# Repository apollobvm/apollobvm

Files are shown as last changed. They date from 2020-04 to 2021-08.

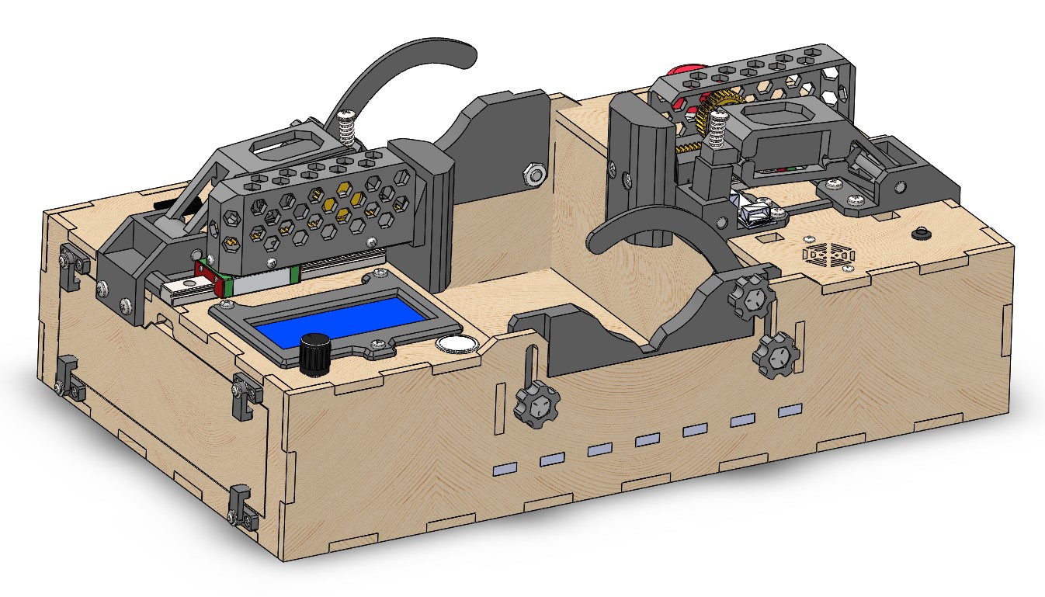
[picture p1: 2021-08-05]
mechanical/Annotation 2020-04-30 215958.jpg

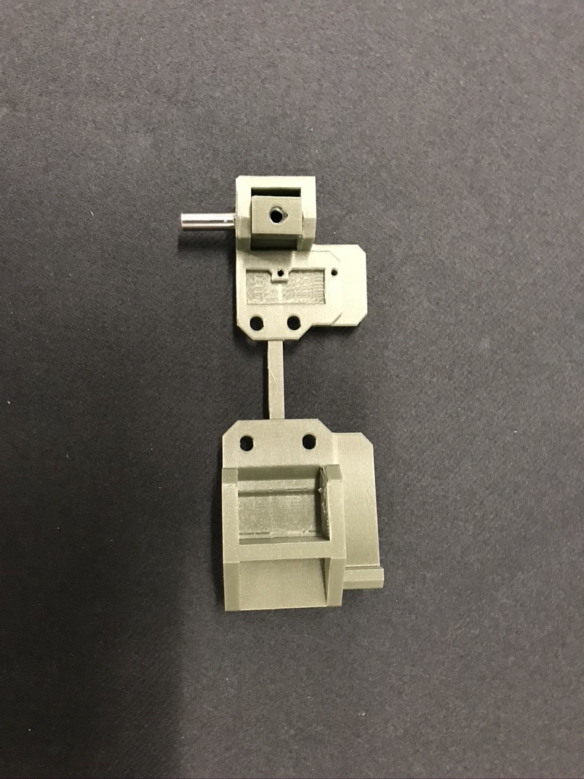
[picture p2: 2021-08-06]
documentation/OEDK - Rice University - ApolloBVM DIY_files/8DABE190-FD51-4D01-BB58-B553A00FD07D_1_105_c.jpeg

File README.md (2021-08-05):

# ApolloBVM - ARCHIVED #
### Rice University Oshman Engineering Design Kitchen ###
###### Author: Thomas Herring ######


<!--[![Build Status](https://github.com/apollobvm/apollobvm/workflows/test/badge.svg)](https://github.com/arduino/arduino-cli-example/actions)-->

**This project is not being actively developed.**

This repository contains all the working code for both the master and slave Arduino to build the ApolloBVM. Feel free to fork it for your own development, we encourage collaboration! All mechanical parts and assembly instructions can be found [here](http://oedk.rice.edu/apollobvm).

For those looking to just download and run the code, please refer to the [releases](https://github.com/apollobvm/apollobvm/releases) section and downloaded the latest firmware. Otherwise, please follow the instructions below on install

For any issues with the code, electrical setup, or mechanical components, please file a bug report [here](https://github.com/apollobvm/apollobvm/issues).

## System Overview ##
The ApolloBVM system uses two coordinated microcontrollers in order to facilitate user input while guaranteeing uninterrupted airflow. The system has a master controller, responsible for managing the display and user input, and a slave controller that actually sends motor commands to the servos. This allows the master controller to operate entirely separately from the slave and ensures that the system is real-time safe. In order to give more clarity about the technical operation of this device, we will outline the operation of each controller separately.

In order to facilitate the various functions of the device, the slave controller operates in 3 distinct states: load, on, and off. While in the ‘load’ state, the slave controller will read ventilation parameters from the master over the I2C bus, generate a new trajectory with these parameters, and turn its state to ‘on’. While in the ‘on’ state, the device will follow the trajectory over and over for infinity. This means that the slave controller will never stop moving the motors unless it receives a command from the master to change its state to ‘stop’. If the master controller were to do so, the device would finish its current cycle and stop moving.

The master controller is mainly tasked with running the user display and sending commands to the slave. Internally, the master switches which panel is currently displaying and manages input from the encoder and buttons. Each panel that the master displays is programmed to follow a different behavior and is modular. This makes it easy to implement panels that behave completely differently and interact with the slave controller on the fly.

## Installation Instructions ##
1. Download the latest Arduino IDE from their website [here](https://www.arduino.cc/en/Main/Software).
2. Download the latest posted release of the device firmware [here](https://github.com/apollobvm/apollobvm/releases), it should look something like "apollobvm_X.X.X.zip".
3. Unzip the downloaded release.
3.  Add the ApolloBVM library to the Arduino IDE:
    1. In the Arduino IDE, go to Sketch->Include Library->Add .ZIP Library...
    2. Navigate to and click on the library zip or library directory inside the extracted release. This will be a file that looks like "ApolloBVM.zip" or a directory with the name "ApolloBVM".
4. Open the slave and master code.
    1. In the Arduino IDE, go to File->Open...
    2. Navigate to and click on the slave.ino file inside the extracted release.
    3. Repeat this process for the master.ino file.
5. Flash the Arduino boards with the firmware.
    1. Plug the first Arduino board into your computer.
    2. In the Arduino IDE, go to Tools->Board and select the Arduino board you are using.
    3. Next, in the Arduino IDE, go to Tools->Port and select the port for your Arduino board.
    4. Push the arrow button to upload code on the Arduino IDE window with the slave code.
    5. Unplug the first Arduino, plug in the second, and repeat the above step for the master code.
6. Follow the wiring diagram on the [ApolloBVM website](http://oedk.rice.edu/apollobvm) to complete assembly.

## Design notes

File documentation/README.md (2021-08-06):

# ApolloBVM Documentation

This directory contrains two website backups that can be viewed locally with
build instructions along with pictures to aid with assembly.

This information is licensed under a
[Creative Commons Attribution 4.0 International (CC-BY-4.0) License](http://creativecommons.org/licenses/by/4.0/).

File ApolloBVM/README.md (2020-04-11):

# Arduino Library for ApolloBVM #

# Credit #
  * Used source code from [Encoder](https://www.pjrc.com/teensy/td_libs_Encoder.html) by Paul Stoffregen Version 1.4.1.
  
# Installation Instructions #
  * In the Arduino IDE, go to Sketch->Include Library->Add .ZIP Library...
  * Navigate to and click on the library zip or library directory inside the extracted release. This will be a file that looks like "ApolloBVM.zip" or a directory with the name "ApolloBVM".

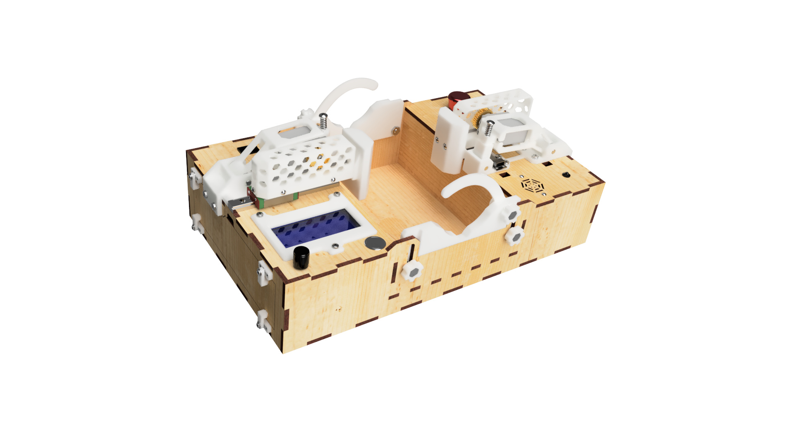
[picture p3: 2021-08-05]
mechanical/ApolloBVM Mk1 - REV1.jpg

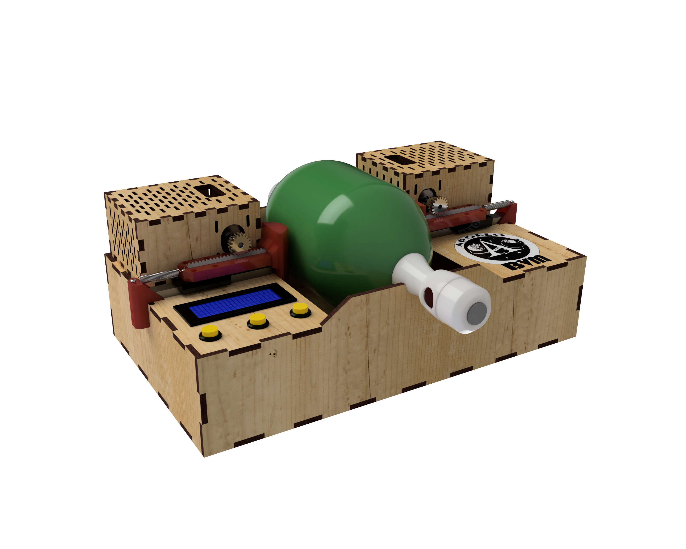
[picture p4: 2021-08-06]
documentation/OEDK - Rice University - ApolloBVM_files/Assem2_OED0011084GX942s_conflicted_copy_2020-03-24_2020-Apr-.jpg

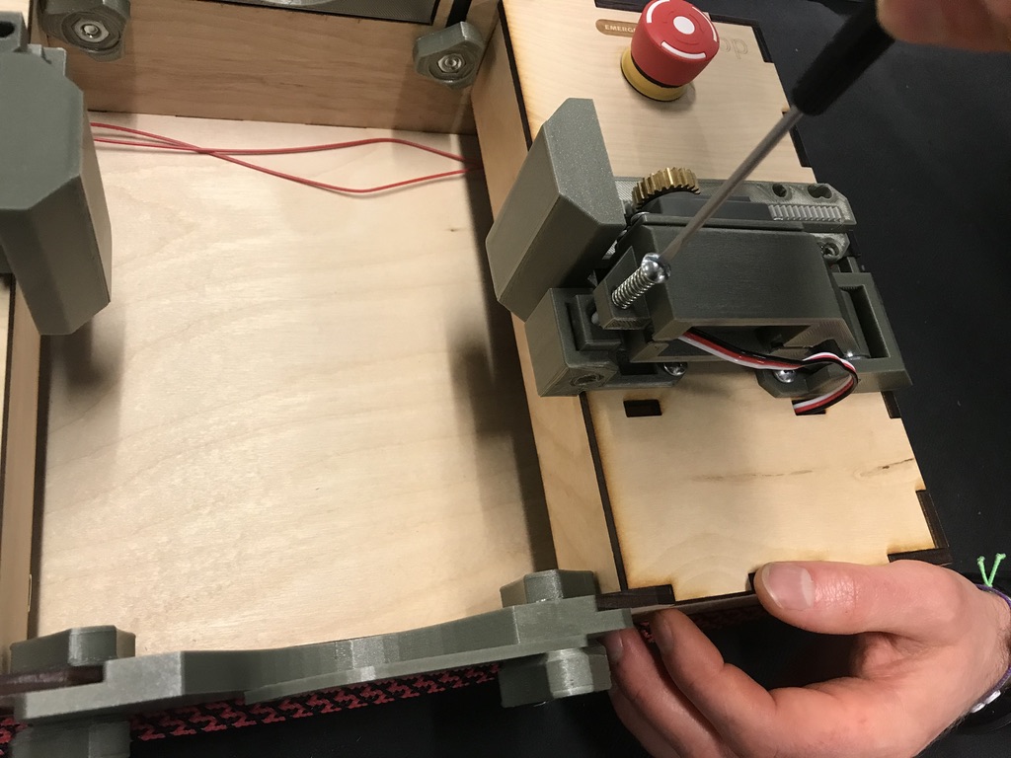
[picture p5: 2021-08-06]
documentation/OEDK - Rice University - ApolloBVM DIY_files/3F8A006A-E7A2-44E5-9089-8951F9FA41A8_1_105_c.jpeg

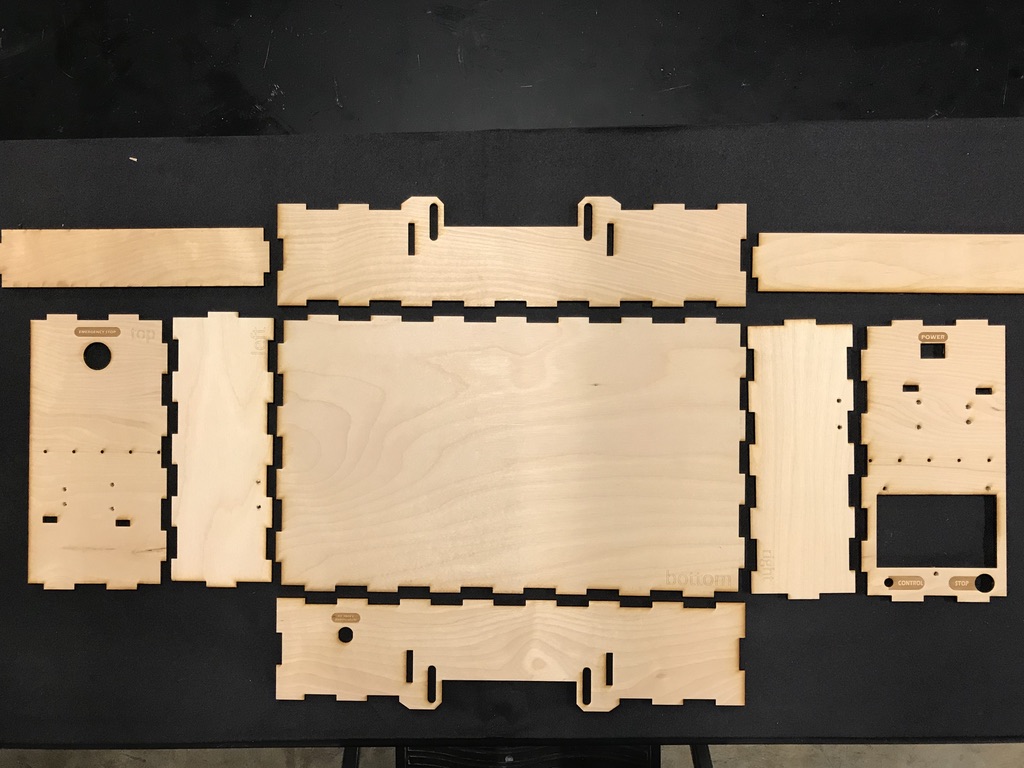
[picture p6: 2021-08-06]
documentation/OEDK - Rice University - ApolloBVM DIY_files/5D290B4A-BDBA-46CC-98D9-BBE2FDADF41D_1_105_c.jpeg

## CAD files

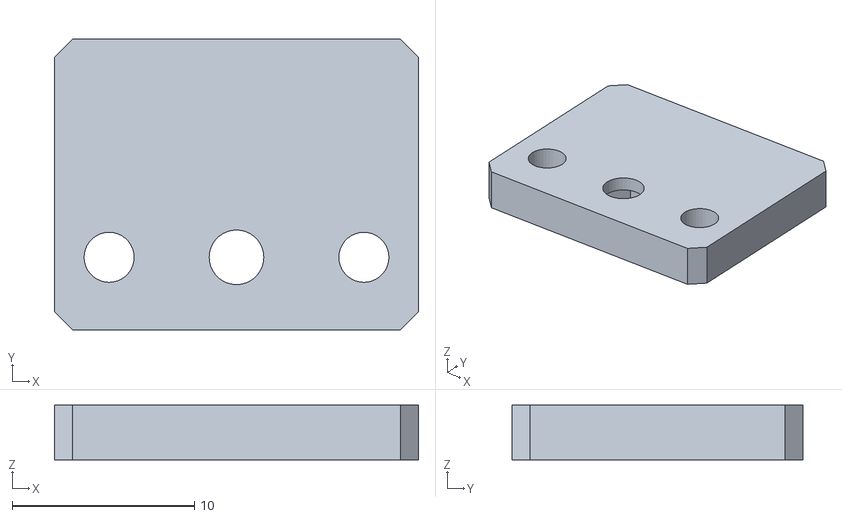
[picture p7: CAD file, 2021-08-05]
mechanical/REV1 STLs/ApolloBVM Mk1 REV1 - Electronics Latch Assembly - Access panel latch - backing.STL
20.0 x 16.0 x 3.00

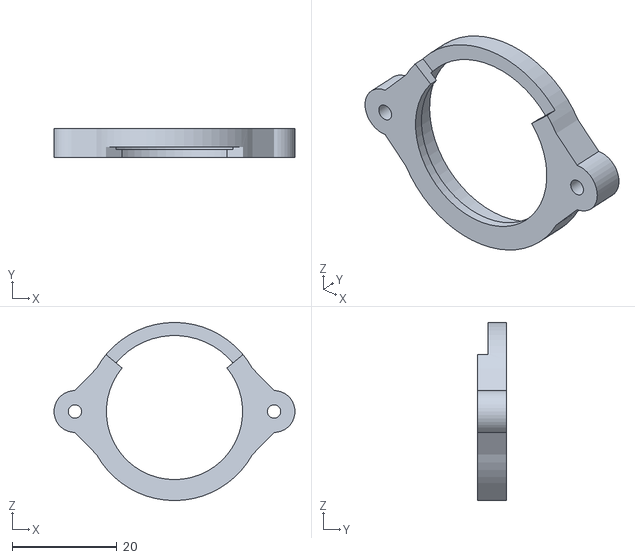
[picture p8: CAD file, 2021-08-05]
mechanical/REV1 STLs/ApolloBVM Mk1 REV1 - Speaker Assembly - Speaker Mount.STL
46.0 x 5.50 x 34.0

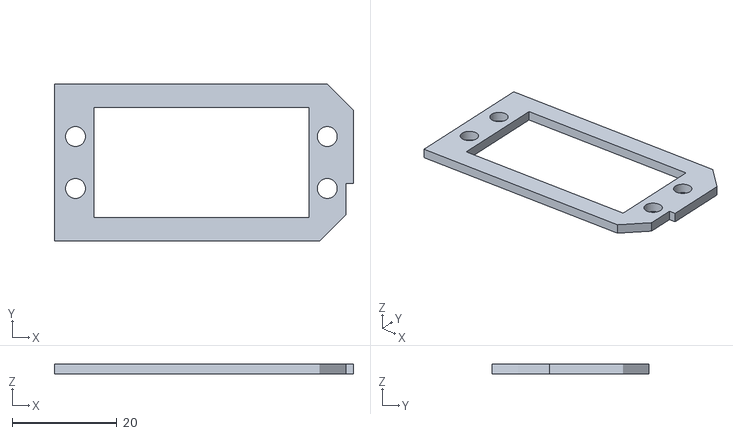
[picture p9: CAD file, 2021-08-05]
mechanical/REV1 STLs/ApolloBVM Mk1 REV1 - Servo Motor Mount Assembly - Servo shim - 2mm.STL
57.0 x 30.0 x 2.00

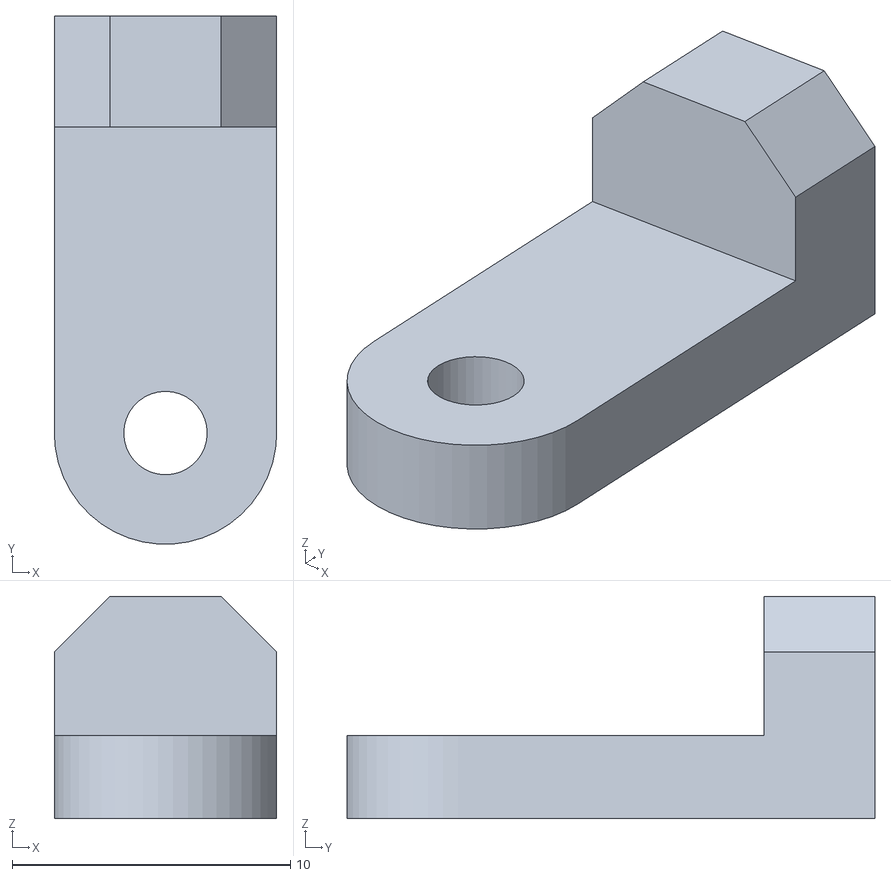
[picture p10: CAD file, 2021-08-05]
mechanical/REV1 STLs/ApolloBVM Mk1 REV1 - Electronics Latch Assembly - Access panel latch - latch.STL
8.00 x 19.0 x 8.00

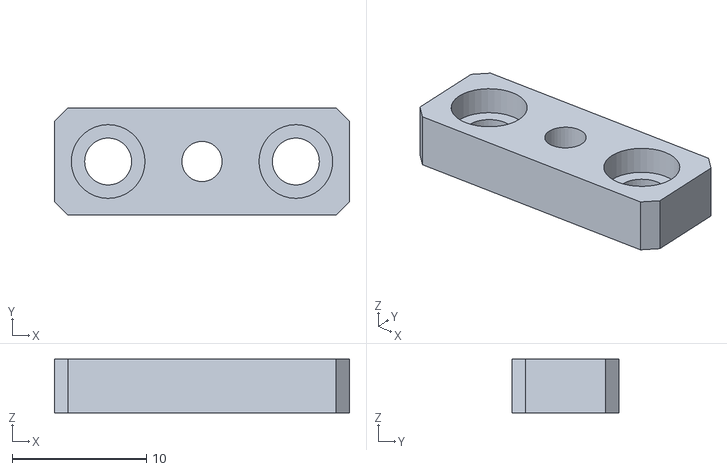
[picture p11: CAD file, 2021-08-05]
mechanical/REV1 STLs/ApolloBVM Mk1 REV1 - Electronics Latch Assembly - Access panel latch - backing front.STL
22.0 x 8.00 x 4.00

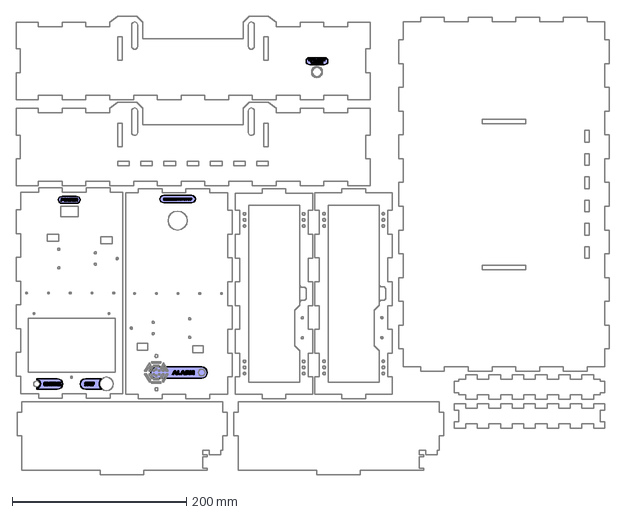
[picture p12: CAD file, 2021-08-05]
mechanical/Laser Cut Pieces/Wood Box - REV1.dxf
680.8 x 526.0 mm

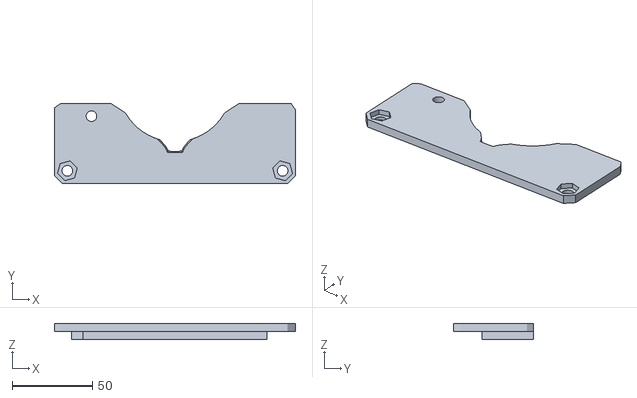
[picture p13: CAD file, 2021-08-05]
mechanical/REV1 STLs/ApolloBVM Mk1 REV1 - BVM Support - Base.STL
150.0 x 50.0 x 10.2

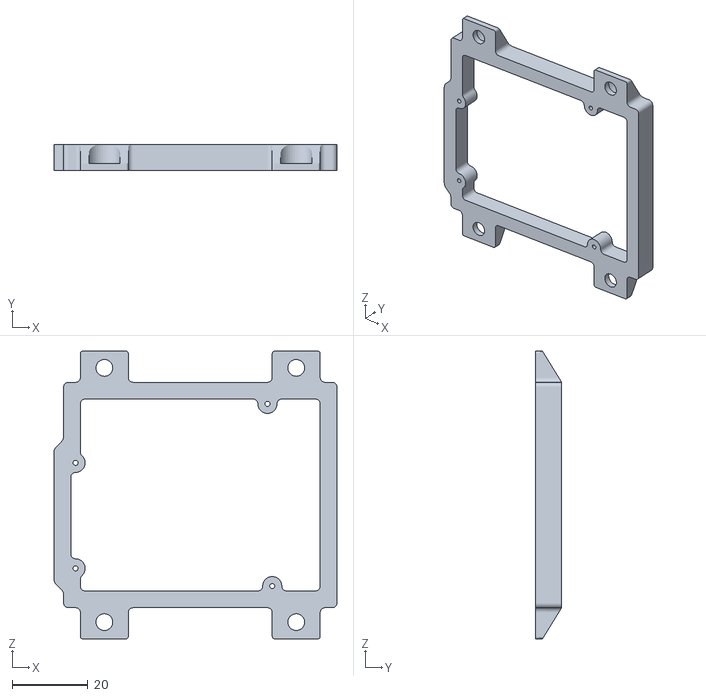
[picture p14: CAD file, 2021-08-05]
mechanical/REV1 STLs/ApolloBVM Mk1 REV1 - Arduino Uno Bracket.STL
74.9 x 6.99 x 76.2

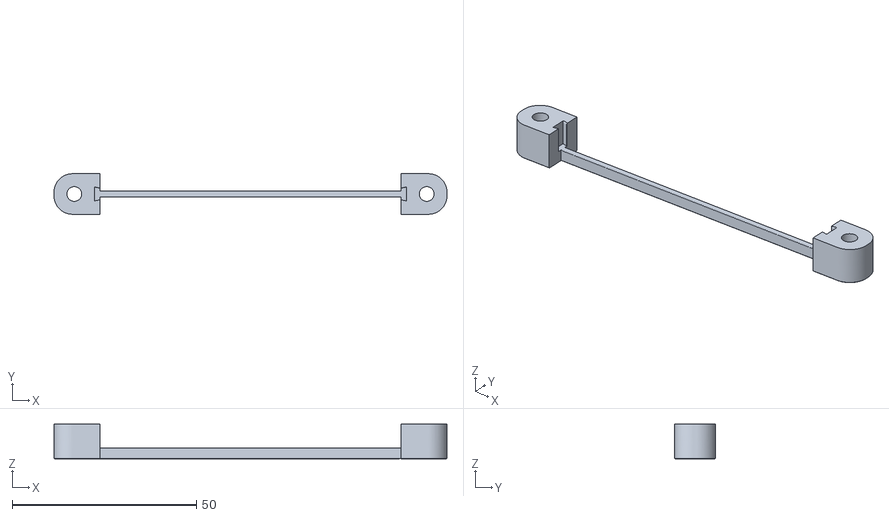
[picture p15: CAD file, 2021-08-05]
mechanical/REV1 STLs/ApolloBVM Mk1 REV1 - Breadboard Brace.STL
106.6 x 11.0 x 9.40

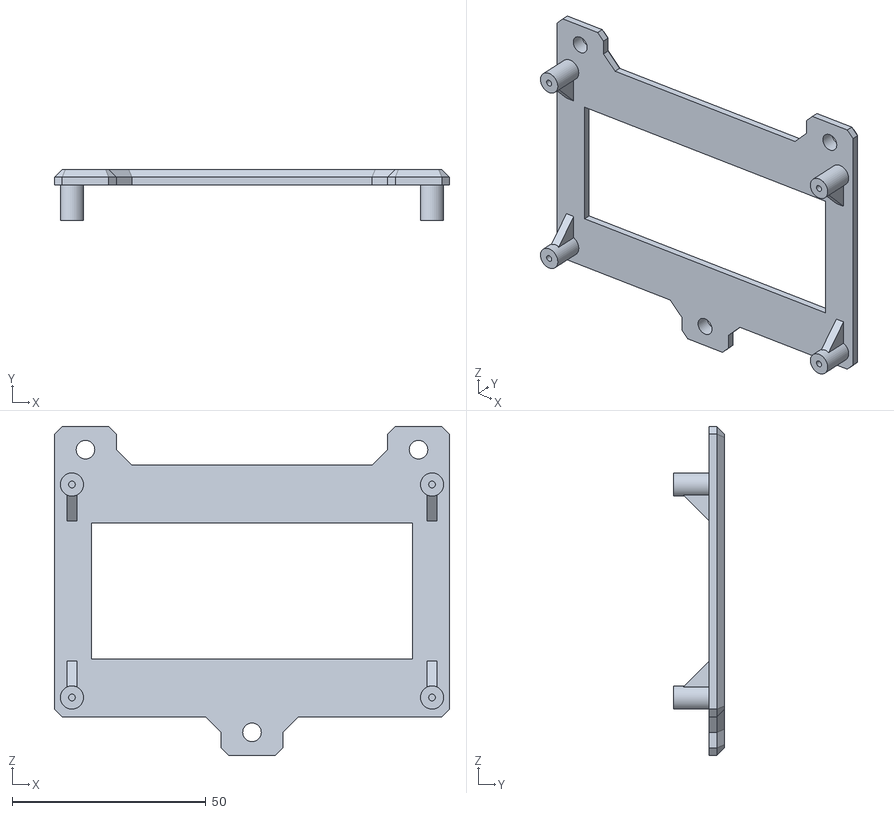
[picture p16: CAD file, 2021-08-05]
mechanical/REV1 STLs/ApolloBVM Mk1 REV1 - Display Cover.STL
102.0 x 13.2 x 85.0

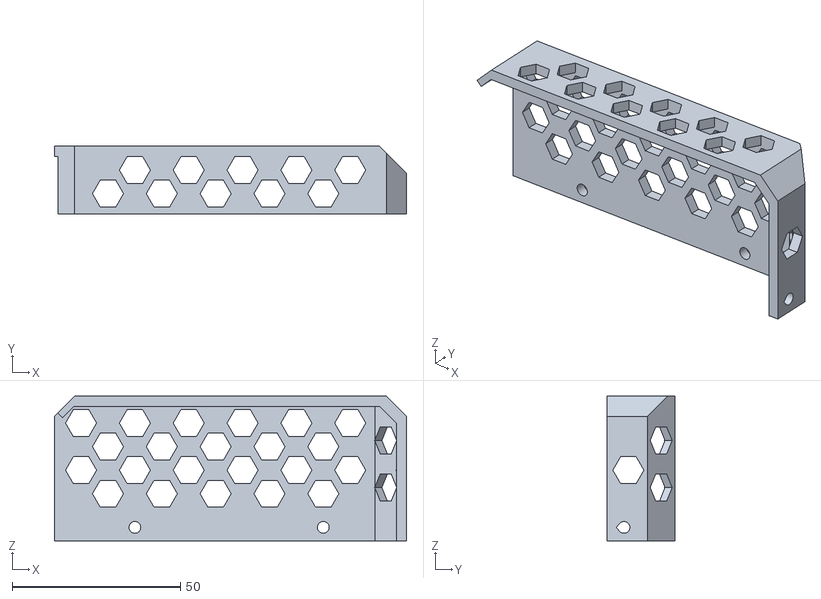
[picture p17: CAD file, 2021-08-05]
mechanical/REV1 STLs/ApolloBVM Mk1 REV1 - Servo Gear Guard.STL
104.6 x 20.1 x 43.0

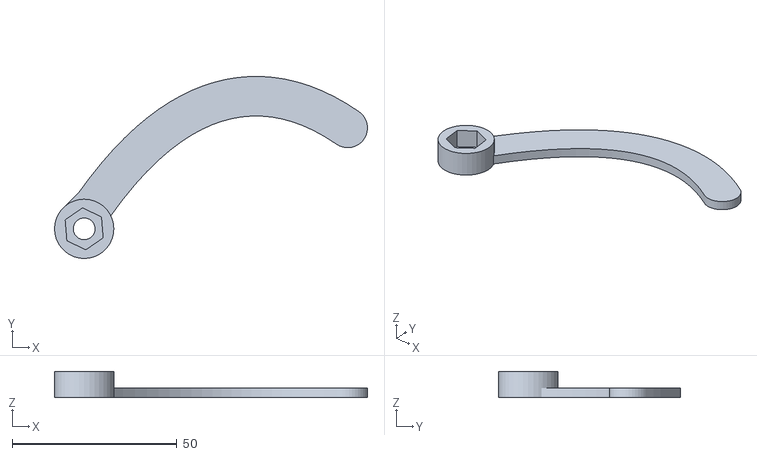
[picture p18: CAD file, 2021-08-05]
mechanical/REV1 STLs/ApolloBVM Mk1 REV1 - BVM Support - Clamp Arm.STL
94.9 x 55.2 x 8.00

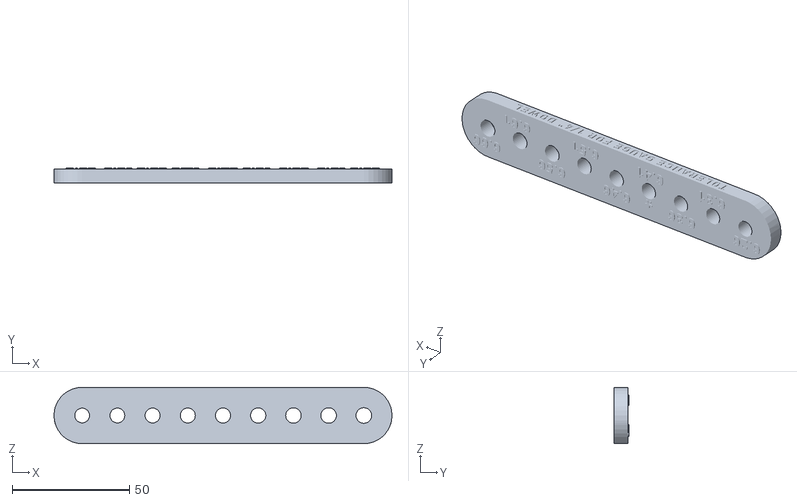
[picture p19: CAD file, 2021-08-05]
mechanical/REV1 STLs/ApolloBVM Mk1 REV1 - Dowel pin tolerance gauge.STL
144.0 x 6.40 x 24.0

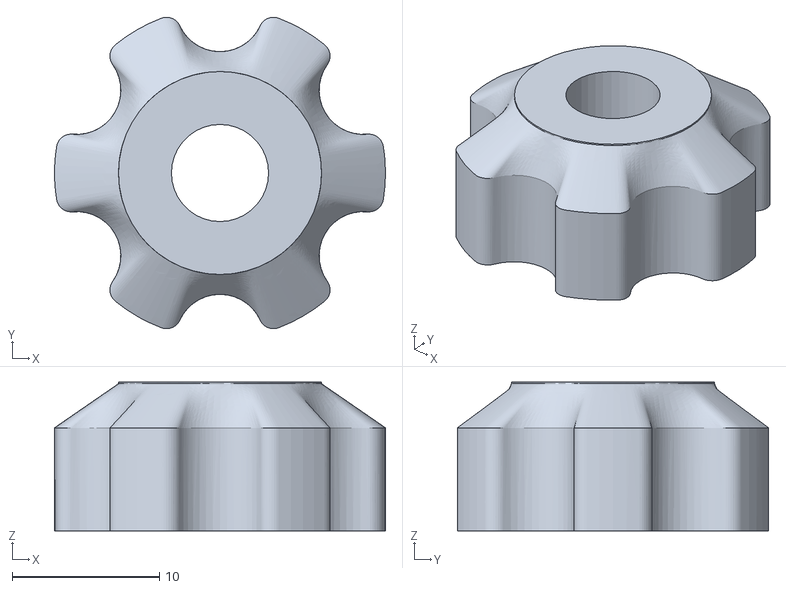
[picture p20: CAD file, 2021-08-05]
mechanical/REV1 STLs/ApolloBVM Mk1 REV1 - Knob - 1_4-20 Hex.STL
22.5 x 21.2 x 10.1

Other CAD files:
mechanical/REV1 STLs/ApolloBVM Mk1 REV1 - Linear Gear Housing Base.STL
mechanical/REV1 STLs/ApolloBVM Mk1 REV1 - Bumper-REV1.STL

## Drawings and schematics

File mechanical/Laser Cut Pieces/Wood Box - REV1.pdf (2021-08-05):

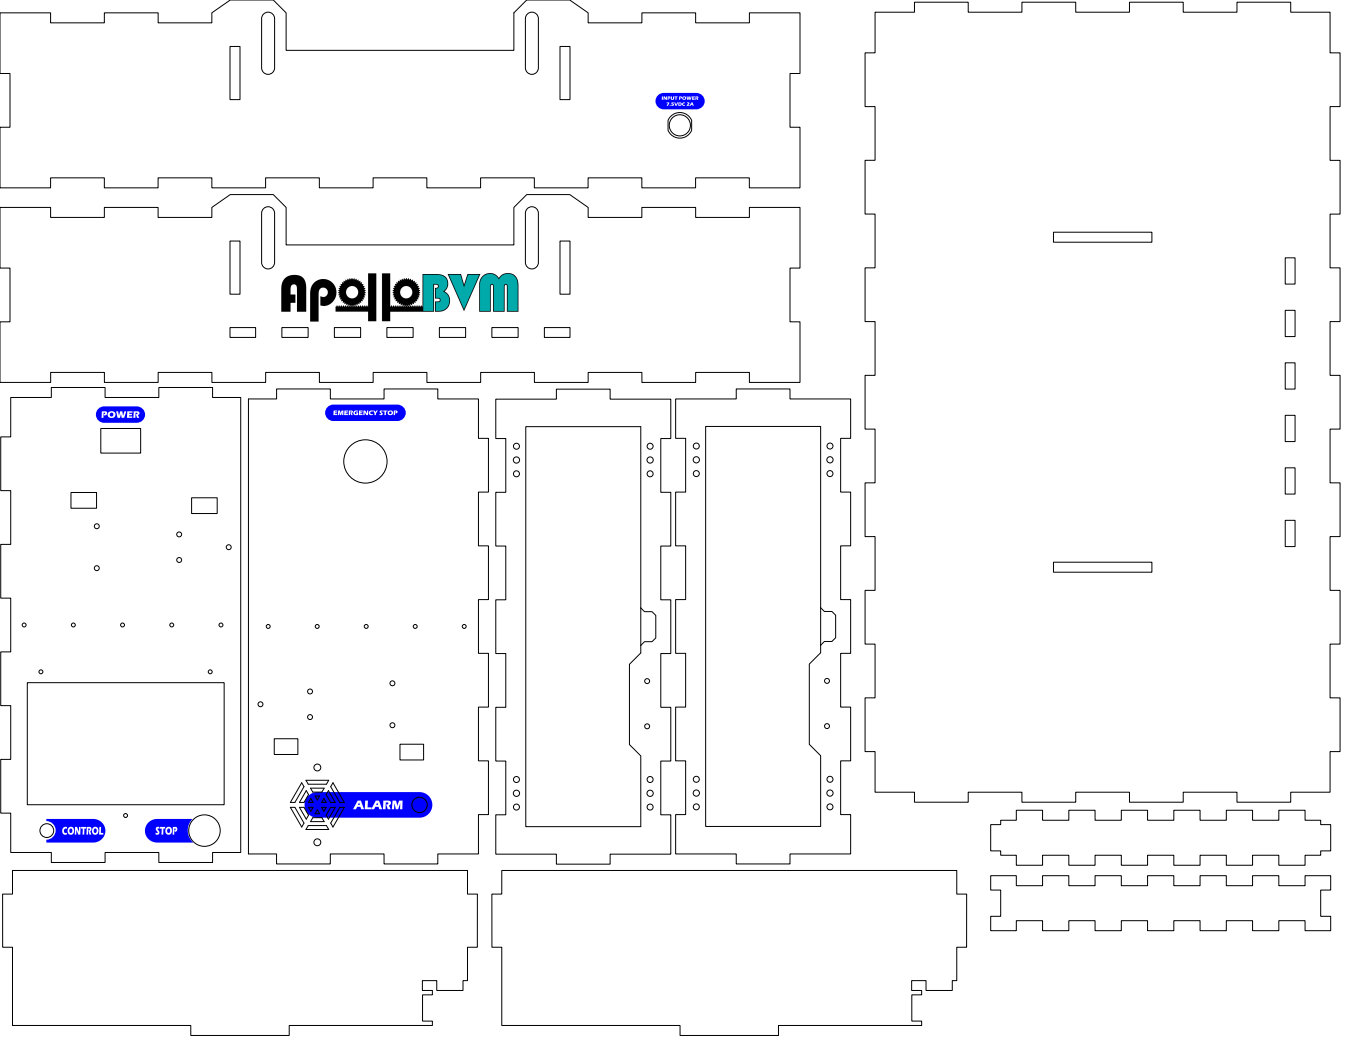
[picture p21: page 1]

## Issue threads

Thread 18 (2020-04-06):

### ISSUE TITLE
Wood laser cutting dimension

### ISSUE THREAD

**Issue by haihaibon** [apollobvm/apollobvm#18]
Could you please adjust drawing dimension? 
![Screenshot_20200405_173556_com autodesk autocadws](https://user-images.githubusercontent.com/63190773/78473472-27bb1700-776b-11ea-9abc-c17313656329.jpg)

**Comment by th3rring** [comment]
Hi there!

Thanks for point this out. We opened the drawings and had no issues with the dimensions. You might have imported them with different units. If you wouldn't mind trying again and seeing if the problem persists. In the meantime, I'm going to close this issue. Feel free to reopen it if you can't find a solution.

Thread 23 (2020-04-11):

### ISSUE TITLE
error compiling master

### ISSUE THREAD

**Issue by Decstv** [apollobvm/apollobvm#23]
'ventlimits' does not name a type: did you mean ventsettings?

error comes up on the release master.

**Comment by th3rring** [comment]
Which release are you using? We tried adding the ApolloBVM library and compiling the master.ino sketch with the latest release and found no issue. We also tried compiling the sketch on Windows and Linux from the master branch and didn't have any problems.

If you're using the current release and having these problems, you might not have added the ApolloBVM library correctly.

**Comment by Decstv** [comment]
Its version 1.1  
As for the library 'ApolloBVM' it is added and included. Can you remove a library and reinstall?

**Comment by Decstv** [comment]
The issue arised during installing the encoder library install. It would not install with the windows version of arduino. I had to uninstall that ver and inatall elegoo ver.

**Comment by th3rring** [comment]
If you wanted to remove a library, you can locate the arduino directory (this is by default in your Documents directory). There will be a directory called "libraries" which contains all the libraries installed for your Arduino IDE.

For the encoder library, you're going to have to scroll down in the library manager and find the exact library that we specified as a dependency. The one we ended up using is "Encoder by Paul Stoffregen", please use the library manager to install this specific version.

**Comment by Decstv** [comment]
OK will do. 

So I guess the root issue is that the encoder library does not work with the windows store version of the arduino app.

**Comment by Decstv** [comment]
Ps. Thank you

**Comment by th3rring** [comment]
I downloaded the windows store version of the program and still didn't have any issues. I'm not totally sure what the issue you're having is but I would recommend going through the installation instructions carefully again just to make sure. If you run into any issues with it, feedback would definitely be appreciated.

I think there are several other people struggling with this library dependency. I'm going to manually move encoder library into the ApolloBVM library to help prevent this in the future. Thanks!

**Comment by th3rring** [comment]
I've gone ahead and made a new release to integrate the Encoder library into the ApolloBVM library. Please remove the old release and download v1.2.0 from [here](https://github.com/apollobvm/apollobvm/releases/tag/v1.2.0). This should fix any issues with dependencies you were having.

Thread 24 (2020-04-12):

### ISSUE TITLE
I'm having problems uploading the firmware to the uno

### ISSUE THREAD

**Issue by shusterm-art** [apollobvm/apollobvm#24]
I get the following message:

master 15:1 error encoder

**Comment by th3rring** [comment]
Seems like you might not have installed the encoder library. Unfortunately, Arduino doesn't let us specify library dependencies. Please refer to the following instructions to install the encoder library dependency:

4. Add ApolloBVM library dependencies.
    1. In the Arduino IDE, go to Tools->Manage Libraries...
    2. In the Library Manager, type "Encoder" into the search box.
    3. Scroll down and locate the "Encoder by Paul Stoffregen" library and then click install.

Let me know if you have any other issues with this.

**Comment by th3rring** [comment]
I've gone ahead and made a new release to integrate the Encoder library into the ApolloBVM library. Please remove the old release and download v1.2.0 from the [releases page](https://github.com/apollobvm/apollobvm/releases). Thanks!

**Comment by shusterm-art** [comment]
Now I get this error message:

master:1:10: fatal error:  panel.h: No such file or directory
  #include  "panel.h"
compilation terminated

I can upload example programs fine.

Any suggestions are much appreciated.  Thanks!

**Comment by th3rring** [comment]
Looks like the Arduino IDE is not finding the ApolloBVM library entirely. Did you follow the directions to add the library to the Arduino IDE?

I'll repost the instructions below for clarity.

3. Add the ApolloBVM library to the Arduino IDE:
    1. In the Arduino IDE, go to Sketch->Include Library->Add .ZIP Library...
    2. Navigate to and click on the library zip or library directory inside the extracted release. This will be a file that looks like "ApolloBVM.zip" or a directory with the name "ApolloBVM".

**Comment by shusterm-art** [comment]
I had the encoder installed.  I was able to load the slave controller but not the master.  Thanks again for the help.  The BVM library is installed.  Not sure what else to do.

**Comment by shusterm-art** [comment]
I finally was able to upload the firmware.  Thank you!

**Comment by th3rring** [comment]
Glad to hear it! Going to close this issue now.

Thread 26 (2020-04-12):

### ISSUE TITLE
What are the pcb components needed for the breadboard?

### ISSUE THREAD

**Issue by shusterm-art** [apollobvm/apollobvm#26]

**Comment by th3rring** [comment]
We've put up a bill of materials and electrical schematic on out [website](http://oedk.rice.edu/apollobvm). You'll have to create an account and sign in to view the materials.

**Comment by shusterm-art** [comment]
Thank you.  I have the BOM for & have everything but couldn't find the specs for the two items added to the breadboard.  Perhaps a diode & cap?

**Comment by th3rring** [comment]
Those should be a 4.7uF capacitor for noise suppression between 5V and ground and a 47k ohm resistor for current limiting on the button.

**Comment by shusterm-art** [comment]
ok.  Thanks.. Are they 100% needed short term testing until I get them?

**Comment by th3rring** [comment]
The 47k ohm resistor is essential, unfortunately. You can use another high value resistor, anything above a couple thousand ohm will be fine.

For the capacitor, we put it on the 5V rail as we noticed a lot of noise from the encoder. You could try without for the time being however if you'd like? I'd still recommend having this there. If you can't source exactly a 4.7uF capacitor, anything around 1 uF - 100 uF or so should be fine.

**Comment by shusterm-art** [comment]
If I can supply 5VDC separately can I eliminate the resistor?

**Comment by th3rring** [comment]
Unfortunately no, the resistor is used to limit the current that's sent through the button and into the Arduino. Again, it doesn't have to be exactly what we specified. We used a 47k ohm resistor as the current drawn when the button is pressed would be 5V/47,000 Ohm = 0.0001 A. You can use anything that pulls a very small amount of current.

**Comment by shusterm-art** [comment]
Thank you for all your help.  I've got the unit up & running.  What is your role on this team?  I sent my info to Mr. Mike Williams about our company Miller Leaman, Inc.  We are building prototypes & have manufacturing capabilities and would like to help.
Marty Shuster
President, Miller Leaman, Inc.
shusterm@millerleaman.com
www.millerleaman.com

**Comment by shusterm-art** [comment]
Thomas,
Thank you for all your help. I've got the unit up & running. What is your role on this team? I sent my info to Mr. Mike Williams about our company Miller Leaman, Inc. We are building prototypes & have manufacturing capabilities and would like to help.
Marty Shuster
President, Miller Leaman, Inc.
shusterm@millerleaman.com<mailto:shusterm@millerleaman.com>
www.millerleaman.com<http://www.millerleaman.com/>
386-562-4121




On Apr 12, 2020, at 5:25 PM, Thomas Herring <notifications@github.com> wrote:

?

Unfortunately no, the resistor is used to limit the current that's sent through the button and into the Arduino. Again, it doesn't have to be exactly what we specified. We used a 47k ohm resistor as the current drawn when the button is pressed would be 5V/47,000 Ohm = 0.0001 A. You can use anything that pulls a very small amount of current.

-

**Comment by th3rring** [comment]
That's amazing! So exciting to see people pick this up and actually build some units. I'm leading the software and electrical engineering efforts on the team here. Mike is one of our media relations specialists and I know he's been quite busy. I'll make sure he gets back to y'all asap however!

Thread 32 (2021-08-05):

### ISSUE TITLE
Archiving the project

### ISSUE THREAD

**Issue by TechnologyClassroom** [apollobvm/apollobvm#32]
I got an email saying, "This project is now being archived.  The ability to login in to get access to the files will be closed on Wednesday, August 4th.  Please download the files, if you wish to continue to get access to them. We will keep the [instructional site](http://oedk.rice.edu/apollobvm) available, if needed."

The mechanical files are currently located on dropbox, but that seems to be going away tomorrow.  It seems the best place for those files would be in this repo or another repo such as <https://github.com/apollobvm/mechanical>.

The [instruction page](http://oedk.rice.edu/apollobvm-diy) behind a login should also be archived along with this maybe as a GitHub page.

**Comment by th3rring** [comment]
Hey there!

Thanks for bringing this to my attention. We actually have also hosted the files on GrabCAD and a link to that can be found [here](https://grabcad.com/library/apollobvm-mk1-rev1-1). I'll also upload the zip file to the repository so it's there. Unfortunately, I'm not planning to work on this project any further but hopefully, there are others that can!

**Comment by TechnologyClassroom** [comment]
It is good to mirror on different sites.  Grabcad requires registration so GitHub would be more accessible.

I was able to download a copy of the website.  If you make a repo for it, I can upload as a PR.  I could do the same for the mechanical repo.

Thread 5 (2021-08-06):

### ISSUE TITLE
Missing documentation and parts

### ISSUE THREAD

**Issue by TechnologyClassroom** [apollobvm/apollobvm#5]
All of the documentation, pictures, and parts from http://oedk.rice.edu/ApolloBVM-DIY should be included on the git or a separate repo.  At this time, there is not a way to collaborate on the rest of the project.

**Comment by th3rring** [comment]
Hi there!

We're not planning on hosting the CAD files right now on Github. We've got a [website](http://oedk.rice.edu/apollobvm) that we've built that includes assembly instructions, videos, and technical documents. Let me know if this isn't effective for your purposes though and we could make some changes to make things more accessible.

**Comment by TechnologyClassroom** [comment]
Requiring registration and keeping the files on dropbox limits access.

Since you already have a github, everything should be available on github and mirrored through whatever other means.  This adds version control and the ability for contributions beyond email.

I can convert the instructions to markdown and submit a pull request to help out with this.

**Comment by th3rring** [comment]
Ya, completely agree. 

The reasoning behind the registration was so that we can keep people in the loop as things progress on our side. We're doing clinical tests today and on Monday so we'd like to be able to easily distribute any findings etc. Also legal here wanted people to have to accept a disclaimer before they've got access to the parts as a precaution.

We're working on trying to have more infrastructure to encourage more collaboration. If you've got any suggestions, they'd definitely be appreciated!

**Comment by TechnologyClassroom** [comment]
With the license, there is nothing stopping anyone from posting the designs on another repo or site as long as there is attribution.  You should post them on your site to keep the project in one place.

Signing up for a mailing list should be encouraged for updates, but should not be a requirement.

**Comment by TechnologyClassroom** [comment]
A quality disclaimer should remove liability.

**Comment by th3rring** [comment]
Thanks for the great suggestions! We'll definitely keep this in mind going forward. I'm going to bring up your feedback with the mechanical team to get their thoughts. 

Going to reopen this issue for the time being as we work this out!

**Comment by TechnologyClassroom** [comment]
Documentation and parts are now part of this repo.  Resolving.

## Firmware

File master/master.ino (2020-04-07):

#include "panel.h"
#include "Wire.h"

// Address of slave.
#define SLAVE_ADDR 8

// Pin definitions.
#define DISPLAY_PIN 3
#define ENC_CLK_PIN 6
#define ENC_DT_PIN 5
#define ENC_BUTTON_PIN 7
#define STOP_BUTTON_PIN 11

// Init peripherals.
NhdDisplay display(DISPLAY_PIN);
Encoder enc(ENC_DT_PIN, ENC_CLK_PIN);
ButtonManager encoder_button(ENC_BUTTON_PIN, true);
ButtonManager stop_button(STOP_BUTTON_PIN, false);

// Default settings.
VentSettings vs = {'X', 500, 12, 1, 3, 0, 00, 20, 0, 0, 0, false}; 

// Default limits.
VentLimits vl;

// Calibration for TV on Ambu bag SPUR II.
int cal[9] = {950, 1062, 1155, 1238, 1320, 1393, 1465, 1538, 1610};

// String params for splash screens.
String* splash_text = new String[4];
String* warning_text = new String[4];

// Init panel pointers.
SplashPanel* splash_ptr;
SplashPanel* warning_ptr;
EditPanel* start_ptr;
EditPanel* apply_ptr;
RunningPanel* run_ptr;
PausePanel* pause_ptr;

// Init display panel pointer.
Panel* cur_panel;

void setup()
{

  // Join i2c bus.
  Wire.begin();

  // Start serial debug connection.
  Serial.begin(9600);

  // Start display.
  display.begin(9600);
  display.clearDisplay();

  // Init slash text.
  splash_text[0] = "";
  splash_text[1] = "     ApolloBVM";
  splash_text[2] = "";
  splash_text[3] = "";

  //Init warning text.
  warning_text[0] = "      WARNING: ";
  warning_text[1] = "   USE ADULT SIZED";
  warning_text[2] = "   BAG VALVE MASK";
  warning_text[3] = "";

  // Init panels.
  start_ptr = new EditPanel(&display, &enc, &encoder_button, &stop_button, &vs, &vl, "Confirm & Run?", &run_ptr, 0);
  warning_ptr = new SplashPanel(&display, &enc, &encoder_button, &stop_button, &vs, warning_text, 2000, &start_ptr);
  splash_ptr = new SplashPanel(&display, &enc, &encoder_button, &stop_button, &vs, splash_text, 2000, &warning_ptr);
  apply_ptr = new EditPanel(&display, &enc, &encoder_button, &stop_button, &vs, &vl, "Apply Changes?", &run_ptr, &pause_ptr);
  run_ptr = new RunningPanel(&display, &enc, &encoder_button, &stop_button, &vs, &apply_ptr, &pause_ptr);
  pause_ptr = new PausePanel(&display, &enc, &encoder_button, &stop_button, &vs, &start_ptr, &run_ptr);

  // Delay just cause.
  delay(100);

  // Set current panel to splash.
  cur_panel = splash_ptr;
  cur_panel->start();

}

void loop()
{

  // Poll button status.
  encoder_button.poll();
  stop_button.poll();

  // Update current panel.
  Panel* new_panel = cur_panel->update();

  // If we get a new panel, start and switch to it.
  if (new_panel != 0) {
    cur_panel = new_panel;
    cur_panel->start();
  }

  // Transmit to the device if necessary.
  if (vs.send)
    transmit();
}

void transmit() {

  // Transmit to the slave device.
  Wire.beginTransmission(SLAVE_ADDR);

  // Write the mode first.
  Wire.write(vs.mode);

  // Send settings to controller unit, if we're loading.
  if (vs.mode == 'L') {
    // Calculate setpoint based on calibration.
    int setpoint = cal[(vs.tidal_volume - vl.min_tidal_volume)/vl.delta_tidal_volume];

    // Send the ventilation parameters to slave.
    Wire.write(byte(setpoint >> 8));
    Wire.write(byte(setpoint & 0x00FF));
    Wire.write(byte(vs.respiration_rate));
    Wire.write(byte(vs.inhale));
    Wire.write(byte(vs.exhale));
    Wire.write(byte(vs.hold_seconds));
    Wire.write(byte(vs.hold_decimals));
    Wire.write(byte(vs.delta_time));

    // Set the mode to on as device will start.
    vs.mode = 'O';
  }

  // Send i2c message.
  Wire.endTransmission();

  // Sent settings so disable send.
  vs.send = false;
}

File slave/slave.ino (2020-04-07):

#include <Wire.h>
#include <Servo.h>
#include <trajfactory.h>

// Address of slave.
#define SLAVE_ADDR 8

// Pin definitions.
#define SERVO_PIN 9

// Limits of servo.
#define SERVO_MIN 2400
#define SERVO_MAX 550

// Init trajectory generation and current pointer.
TrajFactory tf = TrajFactory();
Trajectory* traj_ptr = 0;

// Init servo class.
Servo servo;

// Init current ventilator params.
int rr;
float ie;
int setpoint;
float hold;
int delta_t;
char state;

void setup() {

  // Join i2c bus with address SLAVE_ADDR.
  Wire.begin(SLAVE_ADDR);

  // Register callback function for i2c receive.
  Wire.onReceive(recieveTraj);

  // Start serial output for trajectory monitoring.
  Serial.begin(9600);

  // Attach servo.
  servo.attach(SERVO_PIN);

  // Set state to off.
  state = 'X';
}

void loop() {
  // Run device in different modes.
  switch (state) {
    // Device is on, continue following trajectory.
    case 'O': 
      moveTo(traj_ptr->nextStep(), traj_ptr->getDeltaTime());
      break;

    // Device has been instructed to shutdown.
    case 'X':
      stop();
      break;

    // Device has recieved a new trajectory, load and start.
    case 'L':

      // Stop motion.
      stop();

      // If assigned ptr, delete contents
      if (traj_ptr != 0) {
        delete traj_ptr;
      }

      // Build new trajectory
      traj_ptr = tf.build(rr, ie, setpoint, hold, delta_t);

      // Set device on.
      state = 'O';
      break;
  }
}

void moveTo(int pos, int delta_t){

  // Write current position instruction to console.
  Serial.println(pos);

  // Move the servos to next setpoint and wait delta time.
  servo.writeMicroseconds(SERVO_MIN-pos);
  delay(delta_t);
}

void stop(){

  // If we have already generated a trajectory, follow it till the end.
  if (traj_ptr != 0) {
    while (traj_ptr->getCurrentStep() != 0) {
      moveTo(traj_ptr->nextStep(), traj_ptr->getDeltaTime());
    }
  // If not, got to 0 position.
  } else {
    moveTo(0, 100);
  }
}

void recieveTraj(int num_entries) {

  // Read the state from incoming transmission.
  char recieved_state = Wire.read();

  // Either change machine state or load new settings.
  switch (recieved_state) {
    case 'X':
      state = 'X';
      break;
    case 'L':
      state = 'L';

      // Load new params
      byte high = Wire.read();
      byte low = Wire.read();
      setpoint = (high << 8) | low;

      rr = Wire.read();

      byte inhale = Wire.read();
      byte exhale = Wire.read();
      ie = float(inhale) / exhale;

      byte hold_s = Wire.read();
      byte hold_dec = Wire.read();
      hold = hold_s + hold_dec/100.0;

      delta_t = Wire.read();

      break;
  }
}

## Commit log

2020-04-02 Reorganized library to meet Arduino standard
2020-04-03 Fixed pause panel bug, motor 0 position on boot, and fast traj generation
2020-04-04 Added initial calibration for Abmu bag
2021-08-05 Added mechanical files
    [ApolloBVM Mk1 REV1 - Arduino Uno Bracket.STL, ApolloBVM Mk1 REV1 - BVM Support - Base.STL, ApolloBVM Mk1 REV1 - BVM Support - Clamp Arm.STL, ApolloBVM Mk1 REV1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]
